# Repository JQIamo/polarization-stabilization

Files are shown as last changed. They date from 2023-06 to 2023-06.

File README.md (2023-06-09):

# polarization-stabilization
## Project Outline
This project explores polarization drift in optical fibers and methods for an active compensation system with wavelength division multiplexing. The applications are to long distance quantum communication with polarization-encoded photonic qubits.

## Folder Contents
- Reports:
  - PHYS407_Final_Report.pdf: Summary of project progress through December of 2022. This includes the first round of single wavelength measurements and two wavelength(PMD) measurements.
  - FIO_LS Presentation.pptx: presentation given October 2022 at FIO/LS meeting in Rochester NY
- Polarimeter: documentation for telecommunication polarimeter
  - Polarimeter_Manual.pdf: Describes method of operation, how to use and how to calibrate
  - Electronics: KiCad project files for the Teensy motherboard and photodiode transimpedance amplifier boards
  - Motherboard Box: contains part list, front panel cutout and pcb spacers
  - Photodiode Casing Cage Mounted: FreeCAD and .stl files for the photodiode detector housings
- Scripts
- Single wavelength measurements: All single wavelength measurements made from summer 2022 through spring 2023 are included with a jupyter notebook that performs an analysis.
- PMD Wavelength Measurement: two wavelength measurements made in fall 2022 and analysis script

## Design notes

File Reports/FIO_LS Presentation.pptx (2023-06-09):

## Polarization Drift Compensation for Long Distance Quantum Communication In Optical Fibers

Deven Bowman, Patrick Banner, Deniz Kurdak, Yaxin Li, Trey Porto, Steven Rolston
University of Maryland College Park

## Introduction

- Long distance quantum communication is key to the future of quantum technologies.
- Polarization-encoded photonic qubits are a possible medium for quantum state transportation
  - Easy to apply rotations
- Major problem: polarization drift in optical fibers
  - Mechanical stresses
  - Temperature fluctuations
  - Manufacturing defects

## Drift Compensation System: Overview

- Our system has 3 major parts: input states, polarization analyzer, and the polarization controller.
- I will describe the design/calibration of the polarization analyzer and results of polarization drift measurements.

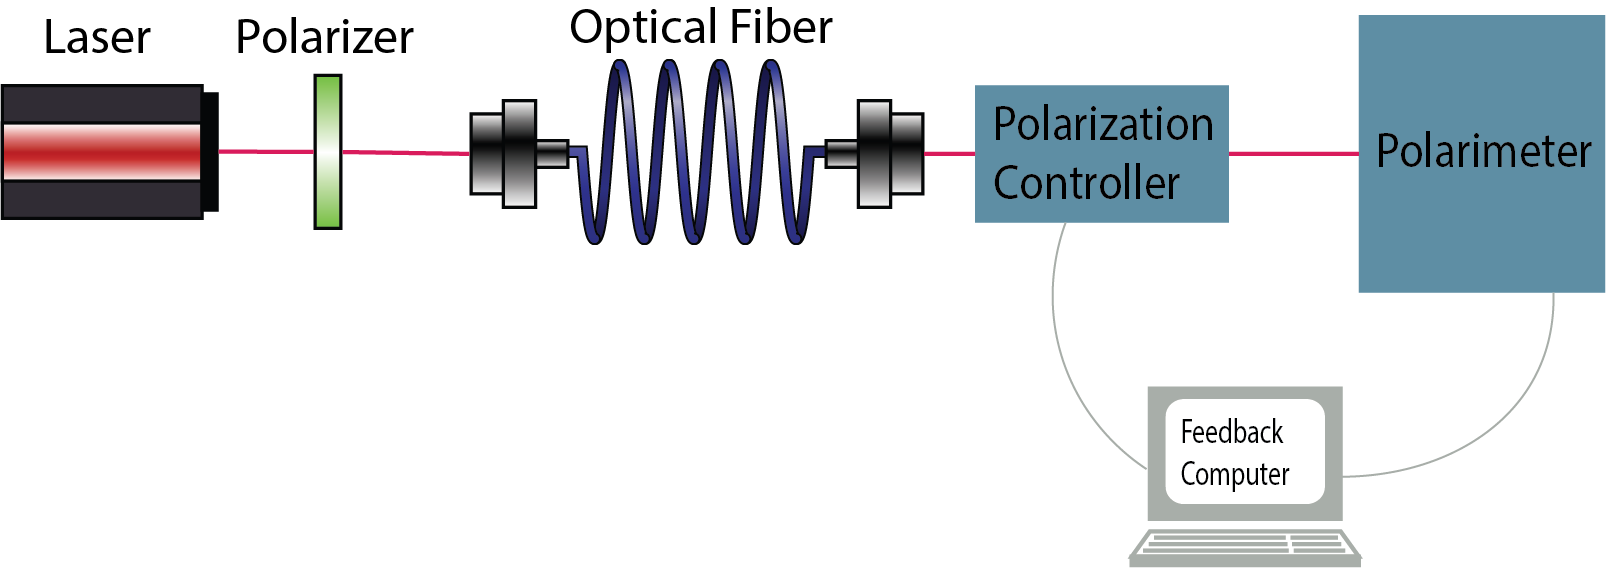
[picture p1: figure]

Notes: Maybe remove text and enlarge image.

## Polarimeter Design

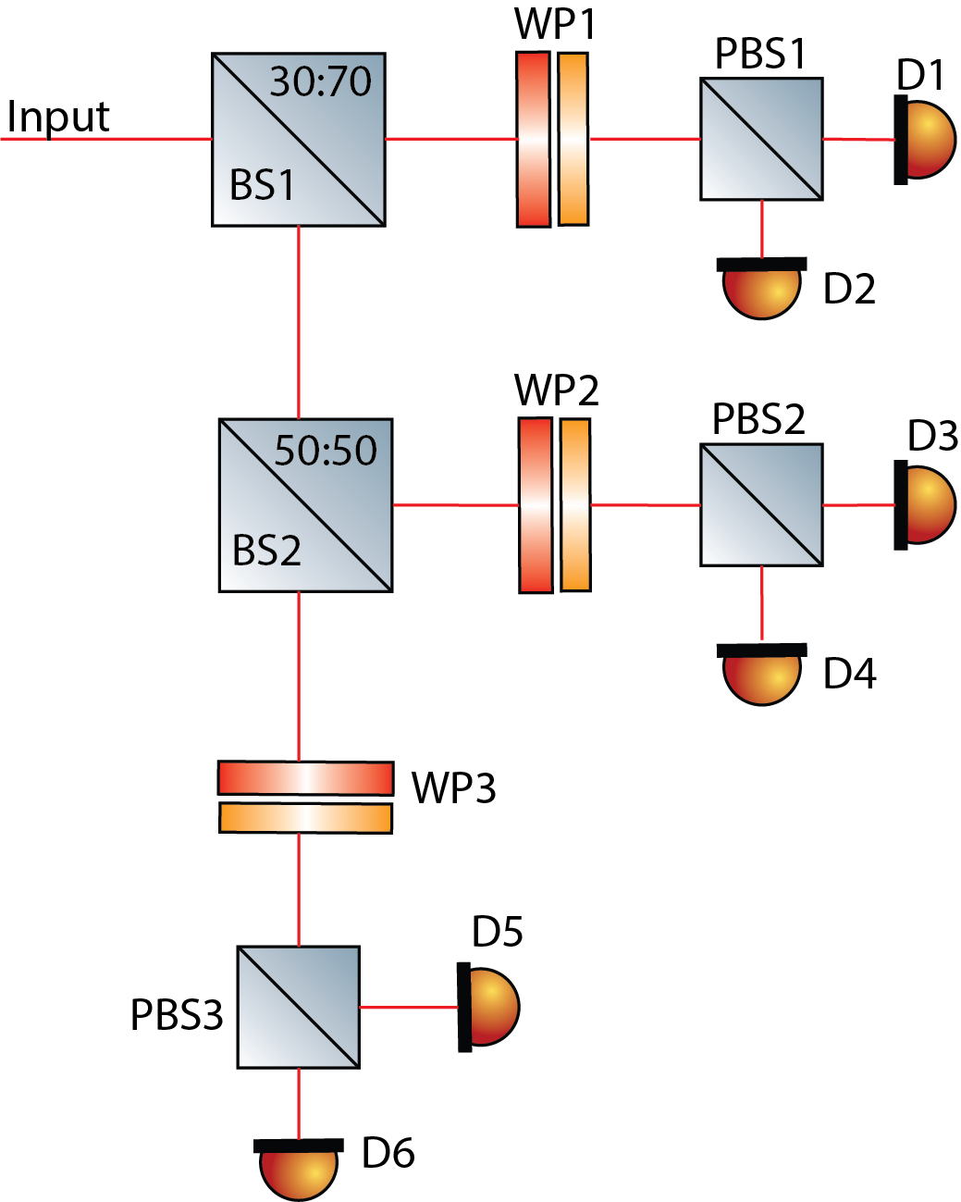
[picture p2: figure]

- 3 detection arms
- polarizing beam splitters project H and V components into separate detectors.
- preceding waveplates “realign” these projection axes

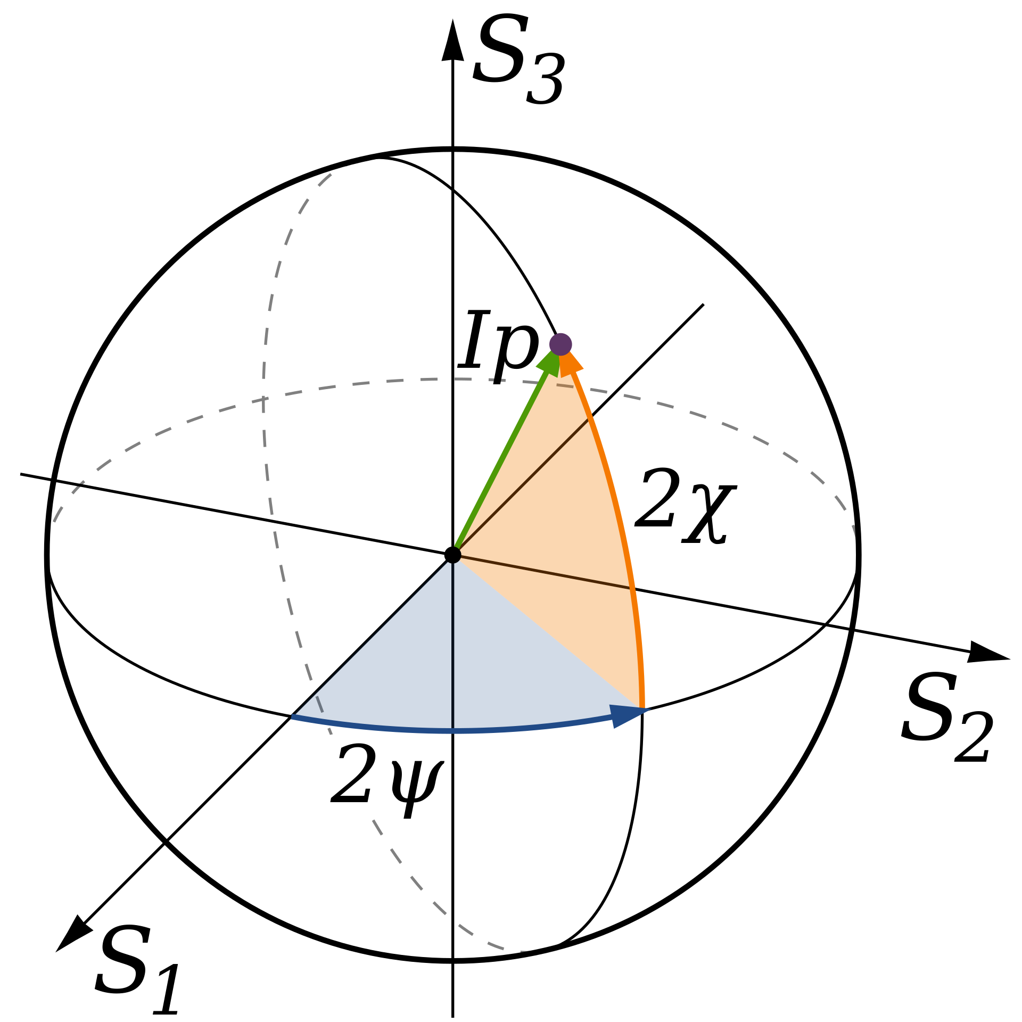
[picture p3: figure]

By Inductiveload - Own work, Public Domain, https://commons.wikimedia.org/w/index.php?curid=4251521

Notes: Adjust diagram: move bottom arm down and add splitting ratio of BS
Perhaps poincare sphere diagram.
Perhaps less words

## Polarimeter Calibration

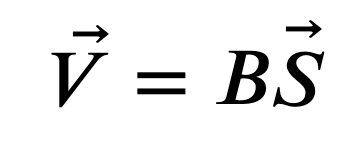
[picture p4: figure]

- Our procedure is based on one presented by Azzam and Lopez, J. Opt. Soc. Am. A(1989).
- The measured state is linearly related to the input state.
- With the Moore-Penrose inverse of this matrix, we can calculate the input states from measurement.

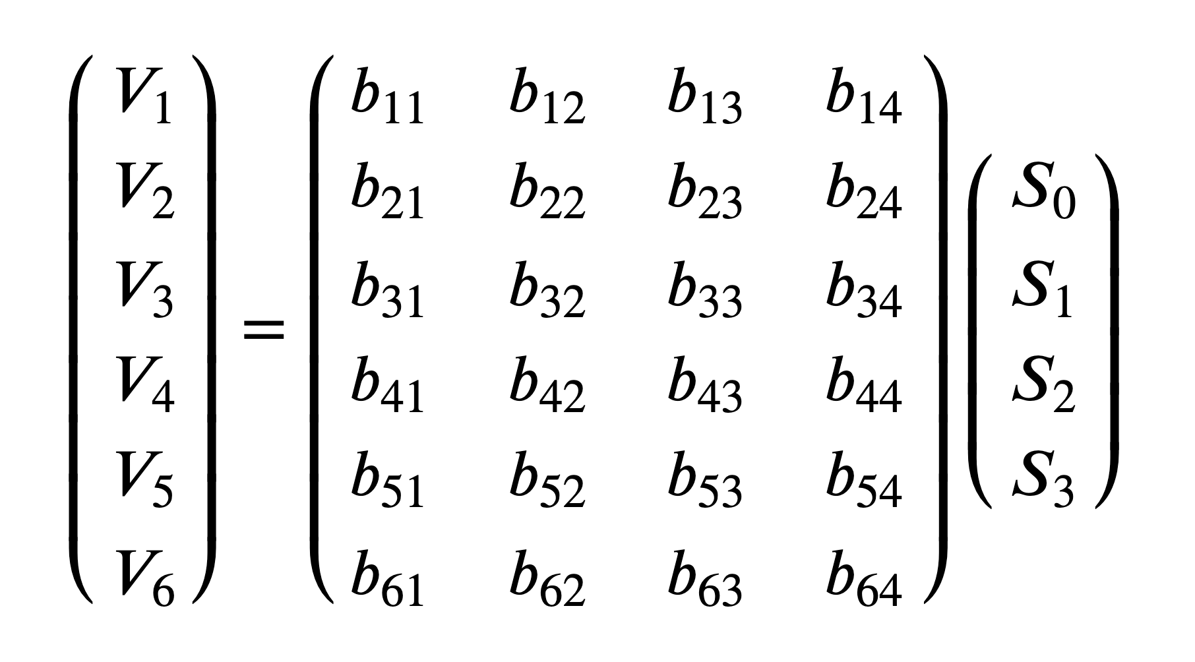
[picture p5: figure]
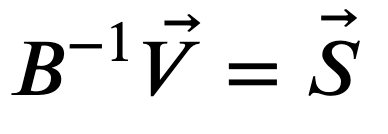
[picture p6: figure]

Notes: Add stokes param slide.

## Calibration Data

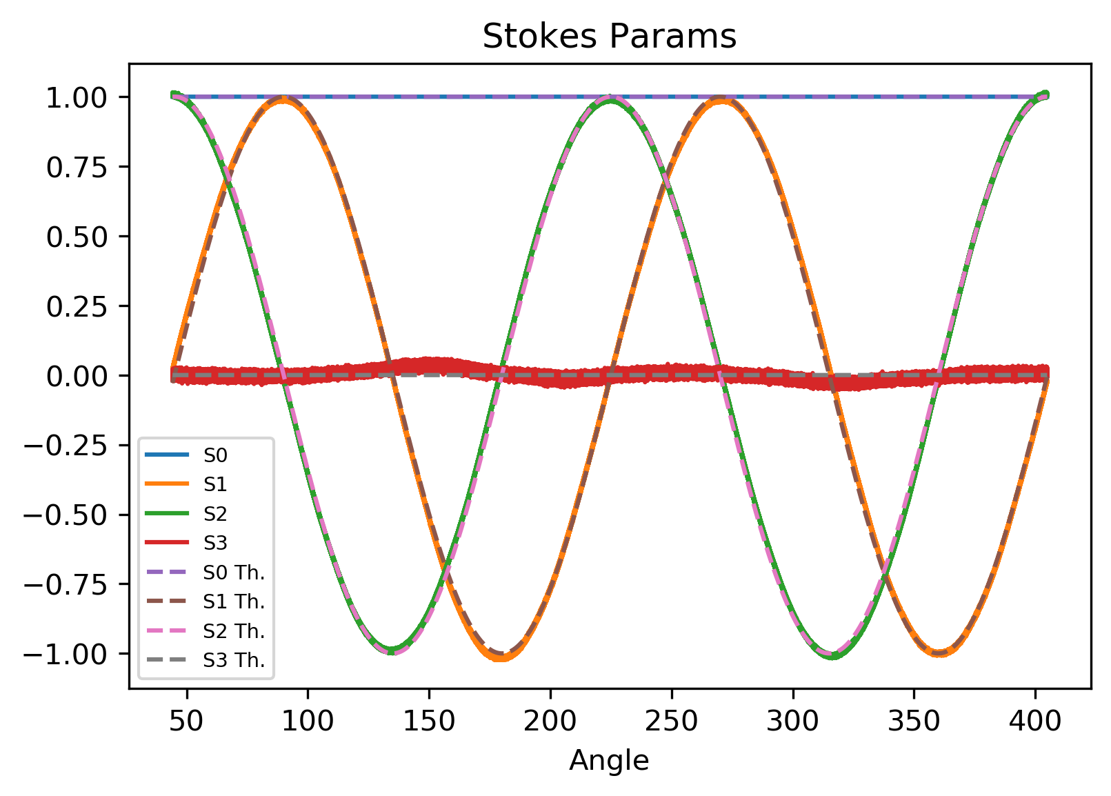
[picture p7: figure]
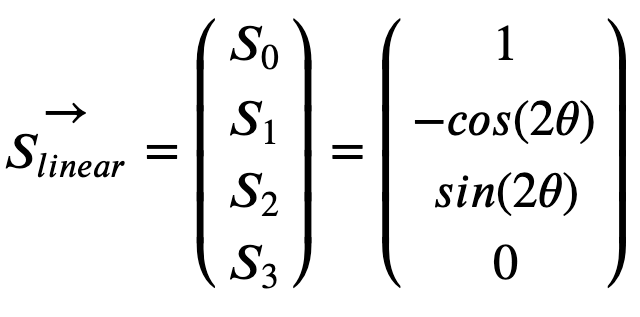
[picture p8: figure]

- A linear polarizer on a motorized rotation mount was used to send in calibration states.
- theoretical Stokes Parameters(dashed lines), calibrated measurements(solid lines).

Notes: Decrease text and move equation

## Polarimeter System

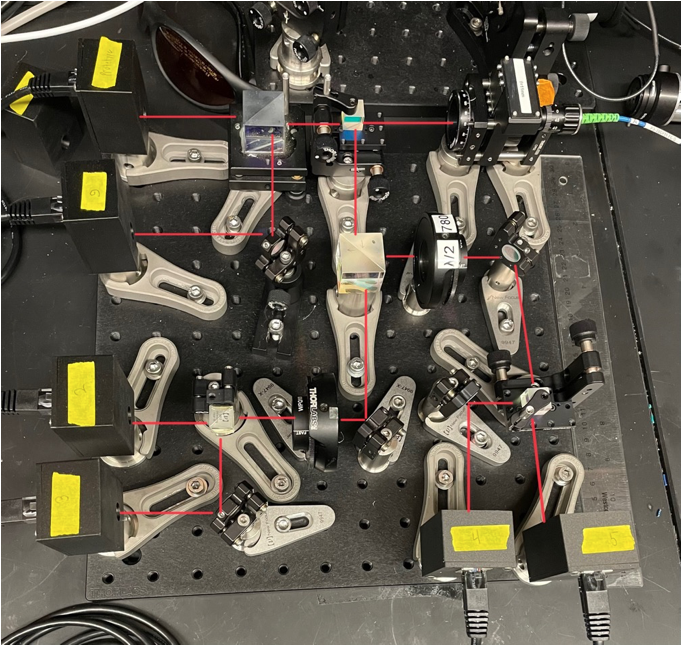
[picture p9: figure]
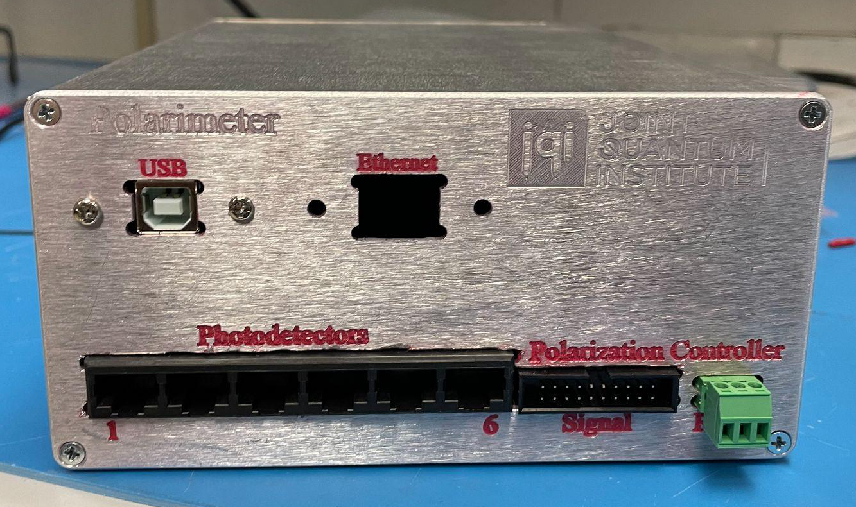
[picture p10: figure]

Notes: Combine with following slide and make more concise. Make read lines bold

## University of Maryland to Army Research Labs fiber link

- UMD and ARL are connected by 2 ~13km fiber optic cables. They are connected on the ARL side for a ~26km fiber loop.
- This fiber provides an optimal test bed for our system.
- Measurements were taken to measure the polarization drift in this fiber. Several other preliminary measurements were conducted for comparison.
- A constant polarization state was launched into the fiber and the polarization was measured on the output by the polarimeter.

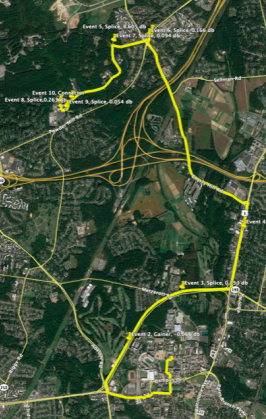
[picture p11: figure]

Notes: Trim words

## Polarization Drift Traces

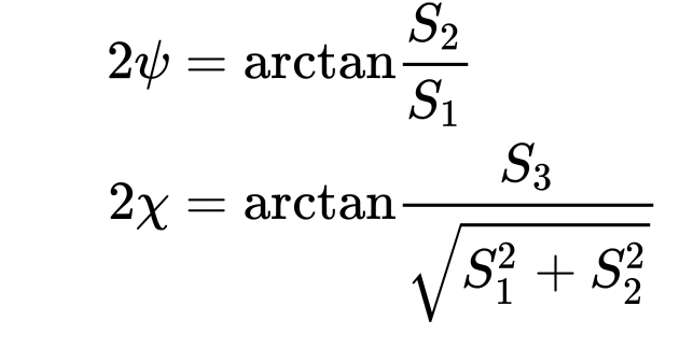
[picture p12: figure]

Direct Connection

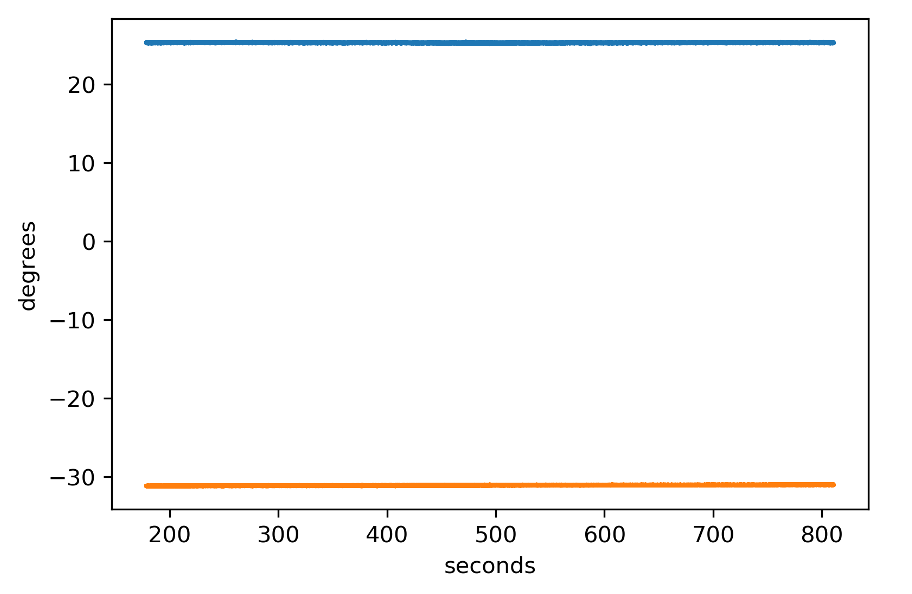
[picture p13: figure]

26km UMD-ARL Fiber

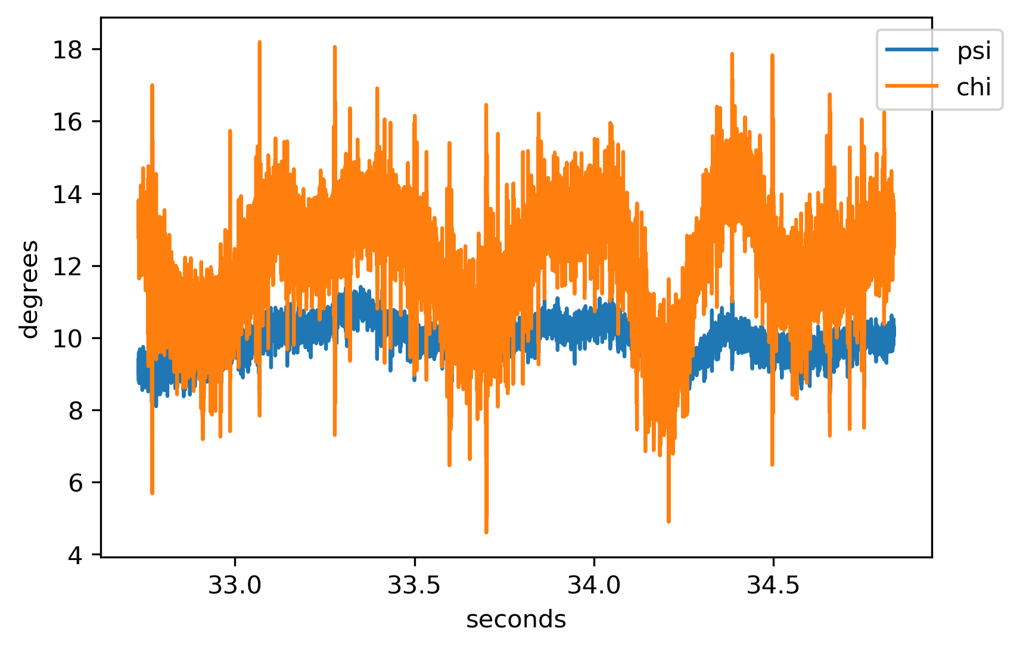
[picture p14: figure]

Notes: Trim words

## Drift Speed Analysis

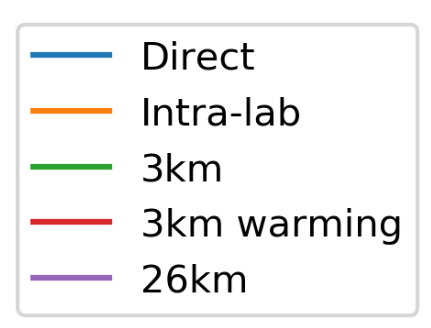
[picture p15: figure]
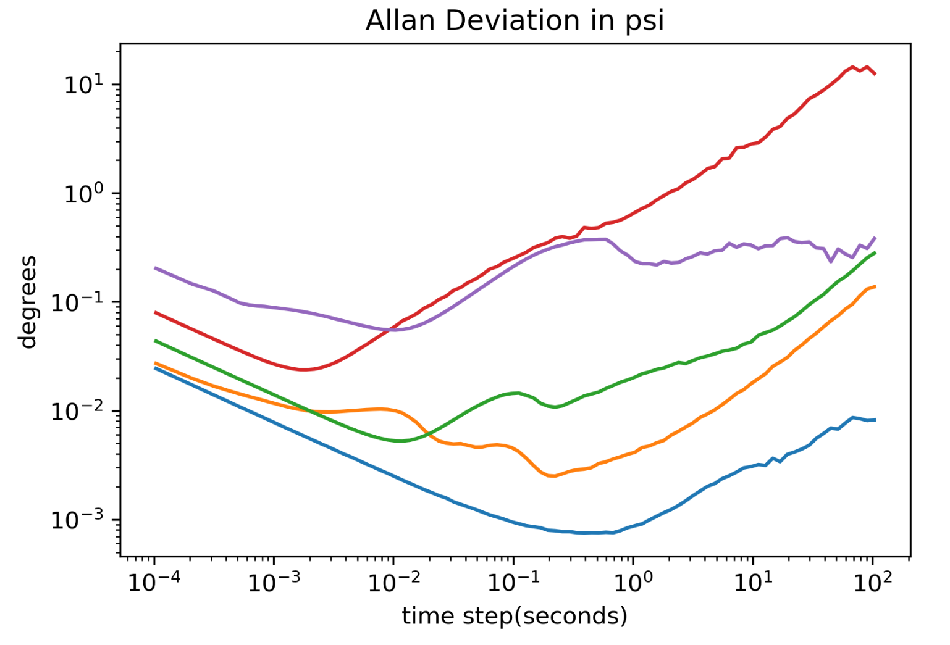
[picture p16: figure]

- An Allan Deviation analysis was conducted.
- Standard deviation between averages over windows of duration τ.

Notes: Don’t try to explain all the lines or to explain allan deviation too technically.

## Going Forward

- Polarization controller feedback algorithm
- Integrate the drift compensation system into a quantum
  - Wavelength Division Multiplexing
  - Polarization Mode Dispersion measurements

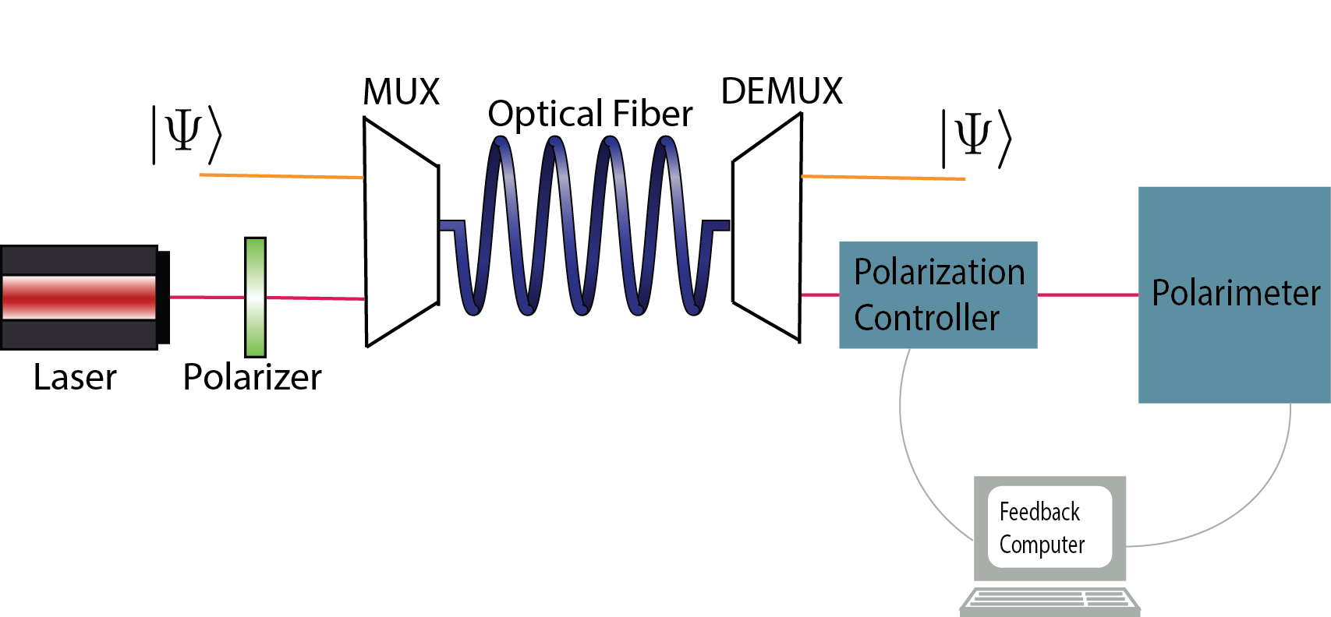
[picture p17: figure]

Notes: Possible a WDM graph?

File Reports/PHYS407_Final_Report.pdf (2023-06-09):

# Polarization Drift Measurements in Optical Fibers for Long Distance Quantum Communication

### Deven Bowman

### June 4, 2023

## 1 Abstract

Polarization drift in optical fibers is studied in the context of developing a polarization drift compensation system for quantum networking atomic systems with > 100 ns long photons. A 26 km fiber, deployed in an urban setting, is used to provide a realistic case study of the polarization drift that will be encountered when trying to achieve long distance entanglement. The rate of polarization drift at one wavelength, 1560 nm, is measured and then compared to measurements of the relative polarization drift between two well separated wavelengths, 1560 nm and 1650 nm.

## 2 Background

Polarization encoded photonic qubits are a natural candidate for a quantum system that can be used to connect nodes of a quantum network. Photons at telecommunication wavelengths can be sent long distances through optical fibers and the transverse modes of polarization form a true two level system that can act as a qubit. Furthermore, qubit operations can be applied with wave plates, an easy to use and ubiquitous technology. This investigation will explore one of the challenges posed to the implementation of polarization qubits, polarization drift in optical fibers.
In general, the polarization state of light is not preserved through optical fibers. Due to mechanical stresses, temperature fluctuations, and manufacturing defects, optical fibers have random birefringences that may vary with time. This leads to the phenomenon of polarization drift and will contribute systematic uncertainty to measurements of the quantum states sent through the fiber. Therefore, understanding and controlling this is of particular interest for efforts to achieve long-distance quantum communication utilizing polarization-encoded photonic qubits.
A polarization drift control system requires several basic elements. Known polarization reference states need to be sent through the fiber under study. The output states are then measured to drive a programmable polarization controller to apply the correct compensating transformation. A major difficulty is to achieve this without interfering with single photons of the quantum channel at their specific wavelength through the same fiber. Previous attempts have addressed this problem by alternating between transmitting single photons and

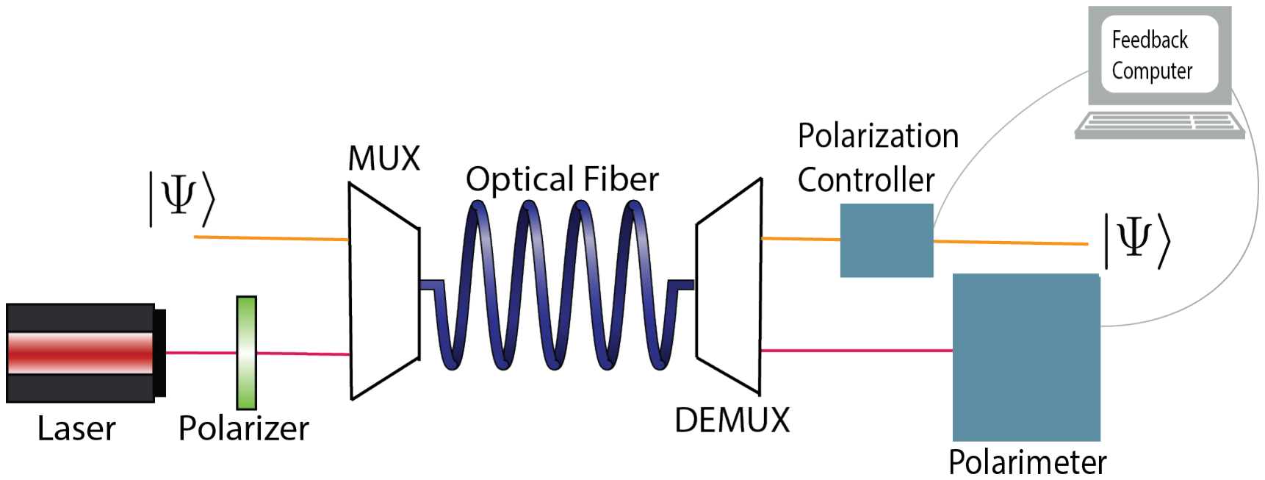
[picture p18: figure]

Figure 1: A wavelength division multiplexing polarization drift control system for quantum communication is displayed. One wavelength is used as the quantum channel while polarization reference states are transmitted at a different wavelength.

transmitting bright reference-state light to stabilize the polarization drift [Wu+06]. If the polarization drift occurs on short time scales, the single-channel method requires interrupting the qubit channel frequently. An alternative method, displayed in Figure 1, is to send reference states at a different wavelength and use wavelength division multiplexing (WDM) so that reference states and qubits are simultaneously transmitted for uninterrupted stabilization.
There are two major concerns for a WDM system: isolation between channels and the wavelength dependence of polarization drift. A milliwatt laser at telecommunication wavelengths, reasonable for transmitting reference-state light, produces ∼ 10¹⁵ photons per second. To multiplex this with a single-photon signal requires wavelength filtering with many orders of magnitude of extinction, which can be improved by increasing the wavelength separation, ∆λ. But, polarization drift varies with wavelength and, with large enough ∆λ, becomes uncorrelated after a time, requiring the transformation matrix relating output states on either channel to be remeasured at repeated intervals [KBA00].
WDM systems have been demonstrated with ∆λ = 0.8 nm, small enough to maintain correlation[Xav+08]. To achieve sufficient isolation with such a small separation, Xavier et al. worked with nanosecond length photons and ignored all signals outside of the expected ns-long windows. Atomic systems typically produce photons 10²
- 10⁴
times longer, requiring
increased wavelength filtering by these factors, achievable with a larger ∆λ. Therefore, an investigation into a polarization drift compensation system using WDM with ∼ 10 − 100 nm separation between channels is well motivated and the development of such a system will address a barrier to the integration of atomic systems, ideal for quantum memories and processors, into quantum networks.
In this analysis, we will adopt 1◦ as the important threshold for a polarization drift compensation system to maintain as the upper bound on polarization drift.
Two sets of measurements were performed in this investigation. I measured the magnitude and rate of polarization drift at one wavelength. Next, I measured the relative polarization drift between two wavelengths. The implications of the results to polarization drift compensation systems for quantum networking are discussed and further steps that can be taken to improve this work are suggested.

## 3 Theory

The Stokes parameter description of polarization uses 4 intensity based metrics to fully describe any full or partially polarized state. Stokes parameters are based solely on observables which makes them the description to use when measuring a polarization state.

S⃗ =

S0
S1
S2
S3

(1)

These 4 parameters in Eq. 1 are calculated with simple intensity measurements. S0 is the total intensity of the light. S1 measures the tendency of light to be horizontally polarized(H), S1 > 0, or vertically polarized(V ), S1 < 0. S2 measures the tendency of the light to be linearly polarized in the 45◦ or −45◦ directions with S2 > 0 or S2 < 0 respectively. S3 describes the tendency of the light to be right circularly polarized(R), S3 > 0, or left circularly polarized(L), S3 < 0. A Stokes vector can be written from these parameters to represent any pure or mixed polarization state.

### 3.1 Pure Polarization States

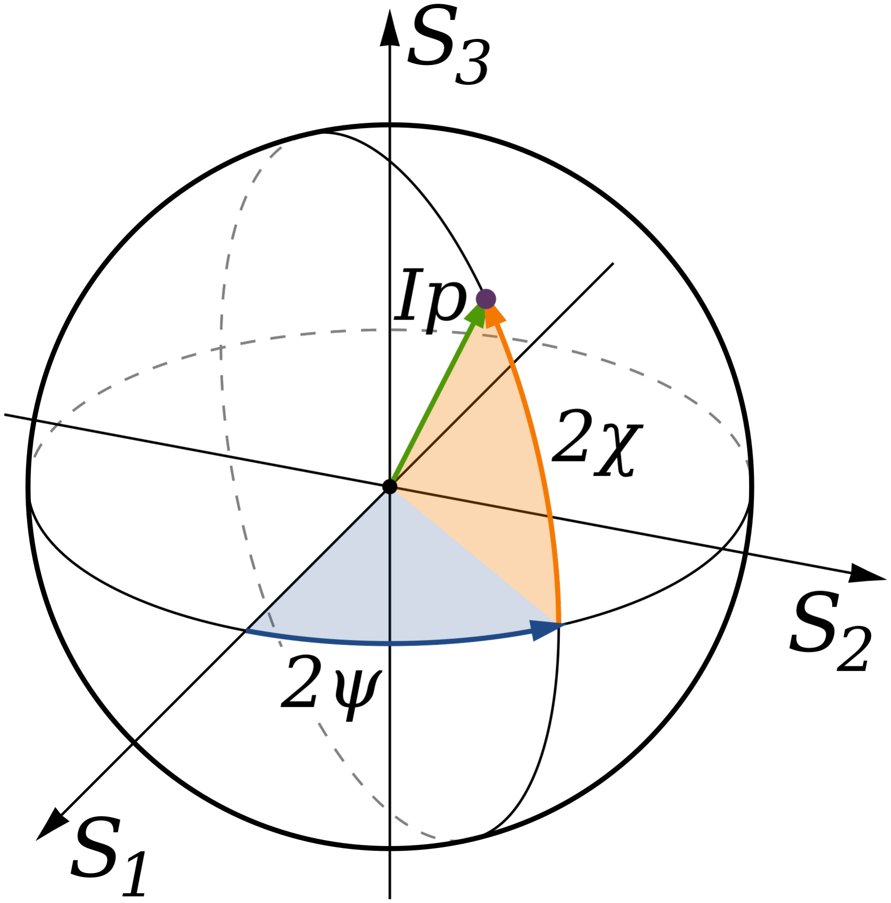
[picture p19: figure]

Figure 2: The Poincare sphere and polarization ellipse angles ψ and χ are displayed.

For pure states, we have the property that S

2
0 = S

2
1 +S

2
2 +S

2/3. As a result, Stokes vectors are often normalized by S0 and reduced to a 3D unit vector.

S⃗ =

1
S0

S1
S2
S3
- (2)

It follows that the set of all pure polarization states can be mapped to a sphere. This mapping is known as the Poincare sphere and is displayed in Figure 2. States on the Poincare sphere can be more concisely represented in terms of two angles.

ψ =

1
2

arctan

S2
S1

, ψ ∈ {0

◦

, 180◦
} | (3)

χ =

1
2

arctan p

S3
S

2
1 + S

2
2

, χ ∈ {−45◦

, 45◦
} | (4)

These angles are formulated to describe the polarization ellipse, but 2ψ and 2χ are the spherical coordinate angles on the Poincare sphere. The factors of two represent that the same polarization state is represented when the polarization ellipse is rotated by 180◦ and when the semi-major and semi-minor axes are swapped.
For the polarization drift and relative drift measurements, we assume that all states are purely polarized since they are generated by laser sources.

## 4 Single Channel Polarization Drift

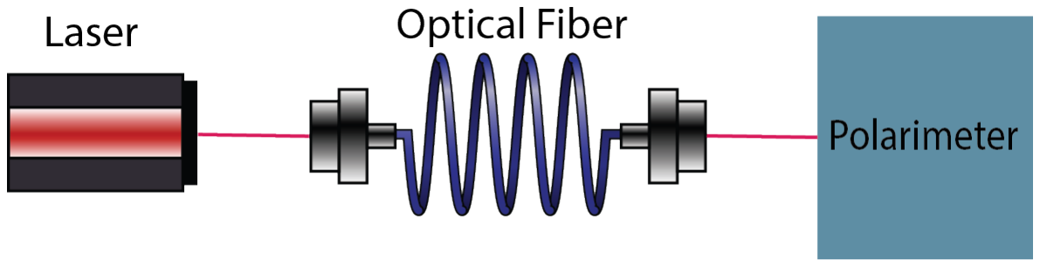
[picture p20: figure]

Figure 3: Schematic for the single channel polarization drift measurement.

To study the rate and magnitude of polarization drift in optical fibers, the experimental setup shown in Figure 3 was used where the length and environmental conditions of the optical fiber was varied. In each measurement, a constant reference state was sent through the fiber with a 1560 nm wavelength laser and the polarization was measured ∼ 10, 000 times per second by a polarimeter custom built for this measurement.

### 4.1 Polarimeter

A six detector Stokes polarimeter was constructed with the schematic depicted in Figure
4. This design uses six intensity measurements that we can relate to the Stokes parameters through a calibration matrix. The photodiode detectors are paired into three detection arms. Light incident on the polarimeter is split into these 3 detection arms by two non polarizing beam splitters, BS1 and BS2. Each detection arm has a series of wave plates, depicted as WP1, WP2 and WP3, that apply transformations to the polarization state before reaching a polarizing beam splitter, PBS1, PBS2, and PBS3, that transmits the projection of the state onto the vertical axis and reflects the projection onto horizontal axis. Finally, a pair of photodiode detectors measures the intensity at each output port of the polarizing beams splitters and produces a voltage signal. While all the PBS’s take projections onto the horizontal and vertical, when combined with the preceding wave plates we can realign their projection axes. The Stokes parameters describe the polarization state relative to 3 linearly independent axes. Therefore, we need to set the wave plates to give us 3 linearly independent projection axes for the different detector arms. Furthermore, the farther we can spread the projection axes in Stokes space, the better the resolution we can achieve. To calculate the

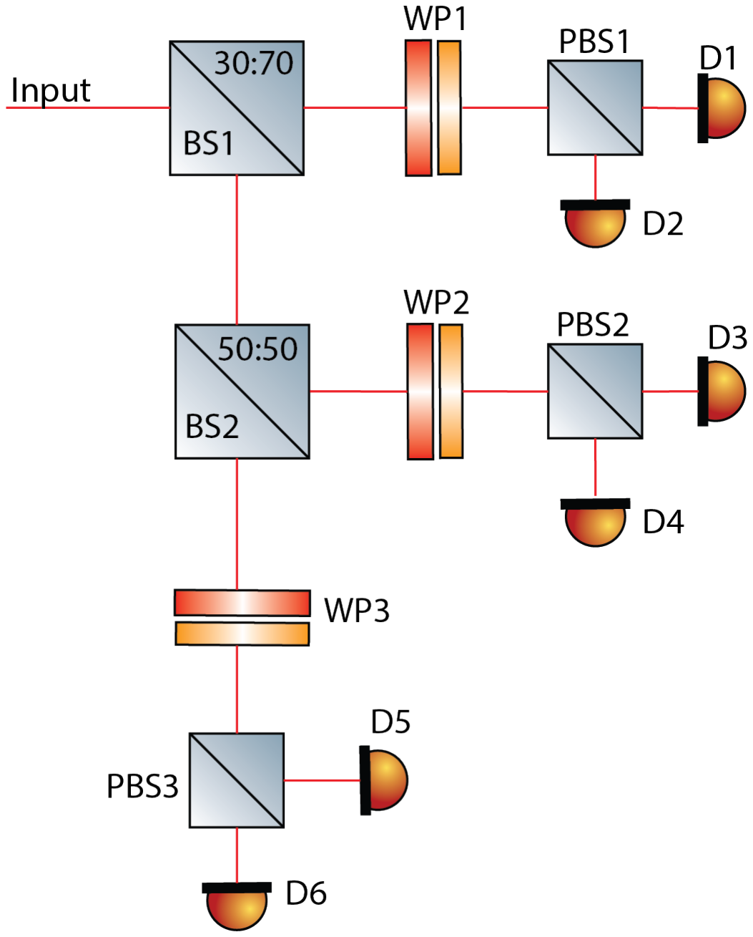
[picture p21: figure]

Figure 4: The design for the Stokes Polarimeter uses several beam splitters (BS), waveplates (WP), polarizing beam splitters (PBS), and photodiode detectors (D) to measure the four Stokes parameters.

Stokes parameters from the output voltage signals we generate a matrix from a calibration procedure similar to that presented by Azzam and Lopez[AL89]. For a polarization state with Stokes vector S⃗, the polarimeter will generate 6 voltages we can write in a vector V⃗ . The two are related by a 6 x 4 matrix B.

V⃗ = BS⃗ | (5)

By generating well defined input polarization states, S⃗ and then measuring the resulting V⃗ , B can be determined. This process was performed in 2 stages. First, a linear polarizer was used to generate a series of known linear polarization states. The input polarization state can be calculated with the angle of the transmission axis of the polarizer from vertical θ with

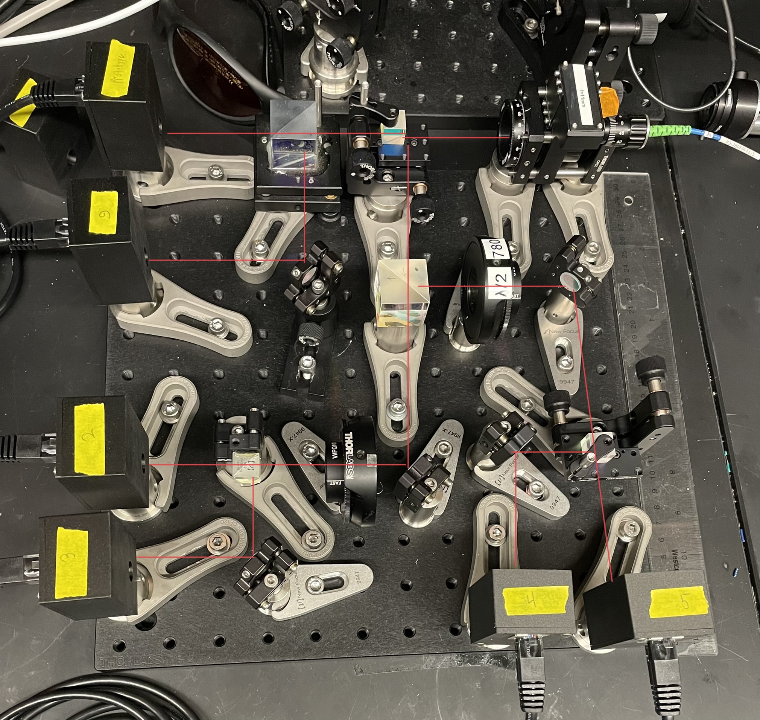
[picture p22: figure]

Figure 5: The 6 detector Stokes Polarimeter is displayed with the optical path drawn as a red line for illustration purposes. The light enters the polarimeter from the fiber launch in the top right. The beam is divided into 6 different paths and the resulting intensities are measured by the photodiode detectors in the black boxes.

Equation 6.

S⃗
linear =

S0
S1
S2
S3

=

1
−cos(2θ)
sin(2θ)
0

(6)

From equations 5 and 6, the i th component of V⃗ can be expressed as a linear combination of matrix elements bij .

vi = bi1 − bi2cos(2θ) + bi3sin(2θ) | (7)

I used a linear polarizer with a measured extinction ratio of > 1000 : 1 and the orientation of the transmission axis known to ∼ ±0.25◦
. The linear polarizer was mounted in a motorized rotation mount and rotated continuously through 360◦ at a rate of 1◦ per second. The polarimeter recorded measurements at 10,000 Hz. A chi squared fit to the measured vi was used to determine the bij matrix elements.
The second stage of the calibration requires input states with some known ellipticity. For this, a procedure, presented in [AL89], was used to account for the error in these input states. First, a linear polarizer and a quarter waveplate were aligned with the transmission axis of the former rotated by 45◦
from fast axis of the latter. In practice, this produces a nearly circular state. Represented on the Poincare sphere, this state is slightly displaced from one of the poles. Then, by rotating both the linear polarizer and the quarter waveplate by 90◦
, the input state is rotated by 180 degrees around the north-south axis of the Poincare sphere. These 2 states are displaced from the pole by a small amount in opposite directions. By averaging the polarimeter measurements associated with each input state, the detector response to a perfect circular state can be attained. By using these calibration measurements, B was calculated which allows the input states to be calculated from the measured voltage states: B

−1V⃗ = S⃗. This calibration matrix, B
−1
, was applied to the voltage states measured from the linear input states. The results are compared to the theoretical values in Figure
6. Good agreement can be seen between the theoretical curves and the measured curves for the normalized Stokes parameters.

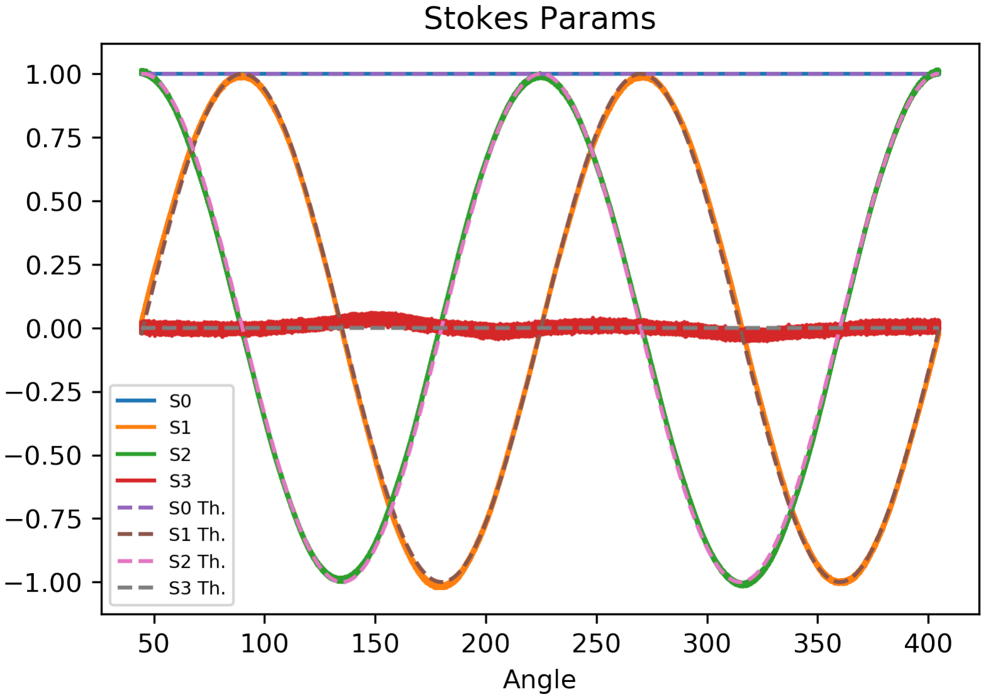
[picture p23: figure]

Figure 6: The normalized Stokes parameters are graphed. The measured parameters are solid lines and the theoretical parameters are dotted lines.

### 4.2 Drift Measurement Procedure

Between the U.S. Army Research Labs(ARL) in Adelphi Maryland and the Atlantic Building at the University of Maryland College Park, there are 2 ∼ 13km fiber connections. Currently these fibers are optically connected at ARL. This 26km fiber, deployed in an urban setting, will be the focus of this stabilization system. A ∼ 2s trace of the polarization data is presented in Figure 8. The polarization state is represented in terms of the angles ψ and χ on the Poincare sphere. A measurement was also taken through a 3 km fiber spool. Measurements were made when the fiber was undisturbed and also when the fiber was forcibly warmed. A trace of the data from the warming trial can be seen in Figure 9. In addition, measurement was made through a fiber connection that stretched across the lab and back to the polarimeter. This was intended to allow for a comparison between the drift in exposed and buried fibers. Only slow drift on the minute time scale was observed in the intra-lab fiber connection. In the final measurement, the polarization drift was measured with the shortest possible connection between the laser source and the polarimeter to provide a baseline for noise inherent to the laser source and the polarimeter. No drift is perceptible in trace from the direct connection configuration, displayed in Figure 7. As a result, our measurements of the polarization drift will have very low systematic uncertainties.

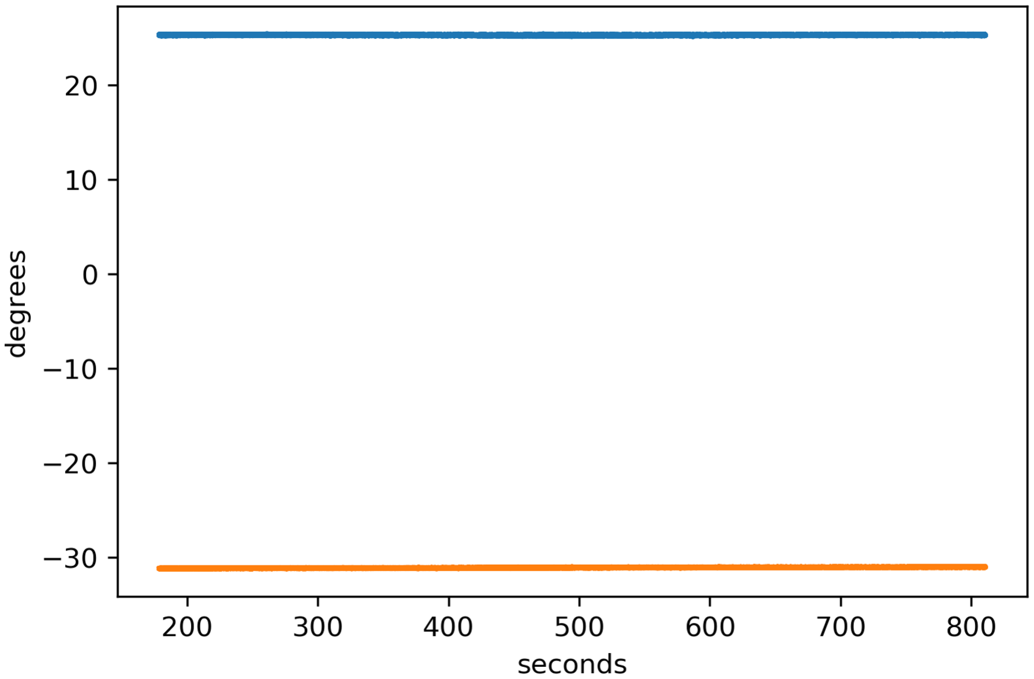
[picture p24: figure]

Figure 7: The output polarization state as a function of time is graphed for a constant input state transmitted through a ∼ 3 m fiber connection.


Figure 8: The output polarization state as a function of time is graphed for a constant input state transmitted through the 26km fiber.


Figure 9: The output polarization state as a function of time is graphed for a constant input state transmitted through a forcibly warmed 3km fiber spool.

### 4.3 Allan Deviation Analysis


Figure 10: The Allan deviation of χ for light at 1650 nm is graphed for the various fiber conditions.

To quantify the drift, the Allan Variance was employed. The Allan variance was devised to measure the stability of atomic clocks over a range of time scales. In a more general context, it is useful to quantify the stability of a measurement in the presence of noise processes. The Allan variance is calculated with equation 8.

σ

2

(τ ) = 1
2

(¯yn+1 − y¯n)

2
=

1
2(N − 1)

N

X⁻¹

i=1

(¯yn+1 − y¯n)

2
(8)


Figure 11: The Allan deviation of ψ for light at 1650 nm is graphed with various fiber conditions.

The data is divided into N consecutive windows of duration τ . The measurements are average within these windows to produce ¯yn, for nth window. The squared difference between ¯yn and y¯n+1 is averaged for all N averaged measurements to calculate σ

2
. With a polarization drift control system measuring and compensating on a time scale τ , we can expect the polarization drift in the fiber to contribute, on average, systematic uncertainties to the qubit channel of order σ. Figure 10 and 11 display σ for each angle over a range of τ from 0.1ms to 100s for the various fiber conditions. The uncertainty in the Allan deviation measurements depends on the type of noise, but it can be well approximated by ± √ σ
N+1 where variances between N+1 ¯y are averaged [RH08].
In all configurations, σ initially decreases. This reflects that the dominant source of noise is random fluctuations from a static distribution. In this range, averaging for longer τ reduces the deviation. Beyond a certain τ , the deviation increases due to noise resembling a random walk process. The measurements of the 26 km fiber show that the deviation reaches a minimum at τmin = 0.01 ± 0.0015 s with σmin = 0.1 degrees for χ. The uncertainty in τ was determined by the spacing between the τmin and the adjacent data points. The Allan deviation was calculated at τ values chosen to be roughly logarithmically spaced at integer multiples of the polarimeter’s sample period. A finer spacing of τ values around τmin can be chosen to reduce the uncertainty, but we are primarily interested in establishing the order of magnitude of the time scale of polarization drift. For this τ , N is large giving uncertainty estimate for σmin of ±8 ∗ 10⁻⁶
for σ, far below the needs of this investigation. Therefore, an optimized polarization drift compensation system should drive a polarization controller with measurements of the drift averaged over ∼ 10 ms windows. This will allow for polarization drift to be maintained below 1◦ on the qubit channel.

## 5 Two Channel Relative Polarization Drift

The same input polarization state at two different wavelengths will, in general, transform through the optical fiber to distinct output states for each wavelength. The relationship between these two output states is expected to vary with time, resulting in relative polarization drift. To measure the relative polarization drift between wavelengths, we need to determine the transformation matrix that relates the output states at either wavelength. Two polarization states were sent through the fiber at each wavelength and the output states were measured. The output states were used to calculate the transformation matrix. Sequential measurements of this matrix allow us to determine the time scales over which polarization drift at either wavelength is correlated.
The polarization transformation induced by the optical fiber can be described as a matrix equation.
T

λjS⃗

λj
i = T⃗

λj
i

(9)

T is the 3x3 transformation matrix of the fiber, S⃗ is an input polarization state to the fiber, T⃗ is an output state, and i ∈ {1, 2, 3}, j ∈ {1, 2} with i indexing the polarization states

and j indexing the wavelengths. By choosing linearly independent input states, {s

λj
i

} and
{t

λj
i

} form bases for the output and input spaces. We can choose the input basis states to be S⃗

λj
1

, S⃗

λj
2

, and S⃗

λj
1 × S⃗

λj
2 where states 1 and 2 are orthonormal and × denotes the vector cross product. Since polarization transformations correspond to rotations on the Poincare Sphere, Tλj (S⃗

λj
1 × S⃗

λj
2

) = T⃗

λj
1 | × T⃗ λi
2 | because Tλj | preserves lengths and angles
between vectors. Therefore, only T⃗

λj
1

and T⃗

λj
2 need to be measured at either wavelength to uniquely determine three output states at either wavelength. Then, the transformation matrix between wavelengths can then be calculated.

T⃗ λ2

i | = MT⃗ λ1
| i

(10)

Equation 10 implies the following relation.

B = MA | (11)

Where the A and B matricies are defined as follows.

A =

S⃗λ1
1

, S⃗λ1
2

, S⃗λ1
3
, B =
| - T⃗ λ2
| 1 , T⃗ λ2
| 2

, T⃗ λ2
| | 3
(12)

Then M can be calculated with A⁻¹ .

M = BA⁻¹
(13)

The schematic for the experimental setup is displayed in Figure 12. Lasers at 1560 nm and 1650 nm are each split into two beams by fiber couplers. At each wavelength, polarization controller fiber paddles transform the polarization state of one beam to be linearly independent with the other beam. A Bristol fiber optic switch launches each beam through the fiber sequentially and a PAX1000IR2 polarimeter measures the output polarization states. The PAX1000IR2 measures polarization states in terms of two angles χ and ψ, defined earlier in terms of their relation to the Stokes parameters, with ±0.25 degree uncertainty up to


Figure 12: The experimental schematic to measure relative polarization drift at 1560 nm and 1650 nm is displayed.

a sample rate of 400 Hz. The PAX1000IR2 was used, instead of the Stokes polarimeter, since it was easier to work with at multiple wavelengths and the speed of the switch was much slower, no longer necessitating the need for ultra-fast polarization measurements. The optical switch is rated to switch in < 5 ms with a switching frequency of 30 Hz. In practice, switching between channels every 150 ms was the fastest achievable rate due to unpredictable latency in either the switching or polarization measurement acquisition. With four channels to switch to, M was measured at every 0.6 s. The experiment was controlled by a Python script that communicated with the optical switch and the polarimeter through serial. Data was collected for 30 minutes.
From the measurements of χ and ψ, it was natural to express the states as normalized Stokes Vectors on the Poincare sphere. In this representation, the M is a 3x3 rotation matrix. Therefore, it can be fully described by an axis of rotation ⃗n and a rotation angle θ. Both of these can be determined from the eigenvalues and eigenvectors of the matrix. The eigenvalues are 1, eiθ, and e

−iθ. The eigenvector with eigenvalue 1, V⃗ real, is parallel to the rotation axis and cos(θ) is the real part of either complex eigenvalue, allowing for determination of θ. V⃗
real
was normalized to be equal to ⃗n up to a sign. The polarization states and θ, were observed to vary smoothly. Therefore, the sign of ⃗n was chosen to maintain continuity. Since ⃗n is also a point on the Poincare sphere, it can be concisely represented in terms of two angles, ψ and χ, giving us a total of three angles that encode the M.
An Allan deviation analysis was performed on these three angles to allow for a comparison to the single channel polarization drift. The Allan deviation is expected to present similar trends to that of the single channel drift. For sufficiently small τ , the M will be measured much faster than the rate at which it drifts. In this range, the deviation will decrease as measurements are averaged over longer τ . At some characteristic time scale τmin, the random walk drift will begin to increase the deviation for longer averaging windows. Therefore, τmin for single channel and two channel relative drift allow for a comparison of the time scales of drift. The Allan deviation results are displayed in Figure 13 for 0.6s < τ < 600s. The


Figure 13: The Allan deviation of the two angles that define the rotation axis, χ and ψ, and the rotation angle. These quantities describe relative drift between channels at 1560 nm and 1650 nm.

lower bound is set by the sample rate of the measurement and the upper bound was limited by the duration of the data taking. The Allan deviation of all three angles present local minima at τmin =∼ 2 s but this approaches the sample rate of the measurement. Therefore, the data provides a coarse set of τ from which we can calculate σ. However, it is clear that the increasing slope characteristic of random-walk noise begins on the several second time scale. For these time scales, the average deviation between rotation angles is ∼ 0.4 degrees and, for ψ and χ, is 0.2 degrees. At τ = 2 s, the sum of all angles is less than 1◦
, suggesting
there is a parameter regime that the WDM system in Figure 1 could operate and maintain less than 1◦ polarization drift on the qubit channel.

## 6 Results

It is clear that the polarization drift at 1560 nm and 1650 nm are not correlated for long times. The transformation matrix between the output states at either wavelengths varies in time. However, this variation may be slow enough to allow for a dual channel WDM system to be implemented. Polarization was found to drift on the 0.1

◦
scale over the 10 ms time scale. By comparison, the relative drift between two channels, in terms of the drift of the three angles that define the transformation matrix, was found to drift by tenths of a degree over seconds. A drift control system could take advantage of the correlation between wavelengths for short times to reduce the rate at which the qubit channel needs to be interrupted. In this system, the transformation matrix between the control reference state channel and the qubit channel could be measured every several seconds. In between these measurements, the polarization drift can be continuously measured on the reference state channel to allow for polarization compensation of the qubit channel. During this window, there will be relative drift between the two channels which will increase the systematic uncertainties on the qubit channel. This investigation shows that these additional uncertainties can be expected to be < 1
- on average.

## 7 Continuing Work

The two channel relative polarization drift measurement will provide more definitive results with a faster sample rate for the measurement. This experiment was limited by unpredictable latency in either the response of the optical switch or the PAX1000IR2 to commands.
I am working on a measurement that should identify either the switch or the polarimeter as the issue. A laser will be sent into one of the ports of the switch while the rest will be dark. A function generator will create TTL pulses to drive the switch between the light and dark channels. A photodiode will measure the output signal on an oscilloscope that is also synchronized with the TTL signal. Varying latency in the switching time will generate a signal on the oscilloscope that is unstable when the trigger is set to the TTL signal.
The sample rate will increase by a factor of four by optimizing the current hardware. This will allow us to probe smaller τ for the relative drift and increase the resolution near

τmin.

## References

[AL89] | R. M. A. Azzam and Ali G. Lopez. “Accurate calibration of the four-detector photopolarimeter with imperfect polarizing optical elements”. In: J. Opt. Soc. Am. A 6.10 (Oct. 1989), pp. 1513–1521. doi: 10.1364/JOSAA.6.001513. (https://doi.org/10.1364/JOSAA.6.001513) url: http://opg.optica.org/josaa/abstract.cfm?URI=josaa-6-10-1513.
[KBA00] | Magnus Karlsson, Jonas Brentel, and Peter A. Andrekson. “Long-term measure- ment of PMD and polarization drift in installed fibers”. In: Journal of Lightwave Technology 18.7 (2000), pp. 941–951. doi: 10.1109/50.850739. (https://doi.org/10.1109/50.850739)
[Wu+06] | Guang Wu et al. “Stable polarization-encoded quantum key distribution in fiber”. In: (2006). doi: 10.48550/ARXIV.QUANT-PH/0606108. (https://doi.org/10.48550/ARXIV.QUANT-PH/0606108) url: https://arxiv. org/abs/quant-ph/0606108. (https://arxiv.org/abs/quant-ph/0606108)
[RH08] | William Riley and David Howe. Handbook of Frequency Stability Analysis. en. July 2008. url: https://tsapps.nist.gov/publication/get_pdf.cfm?pub_ id=50505. (https://tsapps.nist.gov/publication/get_pdf.cfm?pub_id=50505)

[Xav+08] G. B. Xavier et al. “Full polarization control for fiber optical quantum communi-
| cation systems using polarization encoding”. In: Opt. Express 16.3 (Feb. 2008), pp. 1867–1873. doi: 10.1364/OE.16.001867. (https://doi.org/10.1364/OE.16.001867) url: https://opg.optica.org/ oe/abstract.cfm?URI=oe-16-3-1867. (https://opg.optica.org/oe/abstract.cfm?URI=oe-16-3-1867)

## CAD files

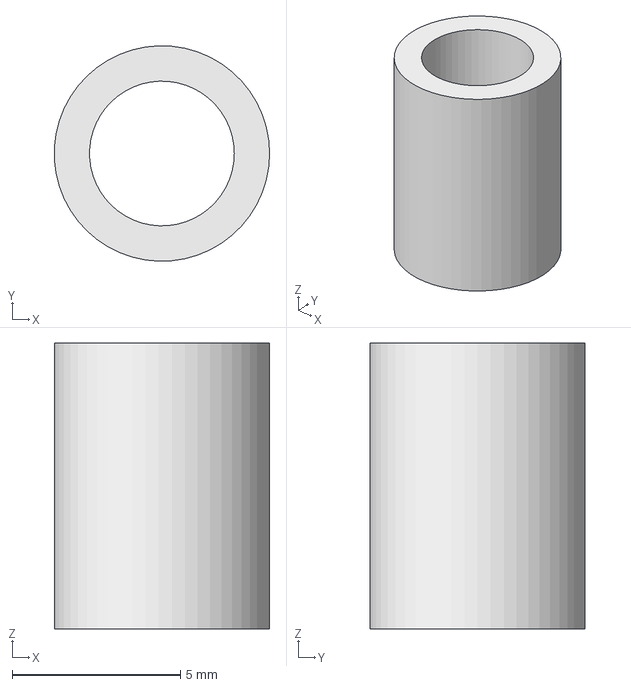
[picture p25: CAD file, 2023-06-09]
Polarimeter/Motherboard Box/PCB Spacers.FCStd
6.39 x 6.40 x 8.50 mm

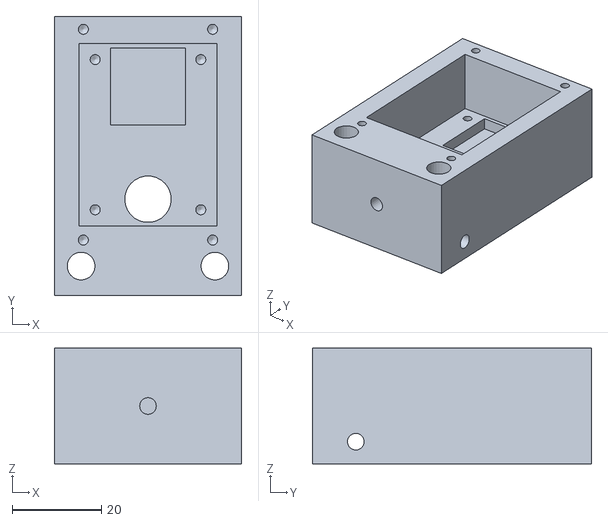
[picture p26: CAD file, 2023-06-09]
Polarimeter/Photodiode Casing Cage Mounted/DiodeCasingCageMounted-Body.stl
42.0 x 62.6 x 26.0

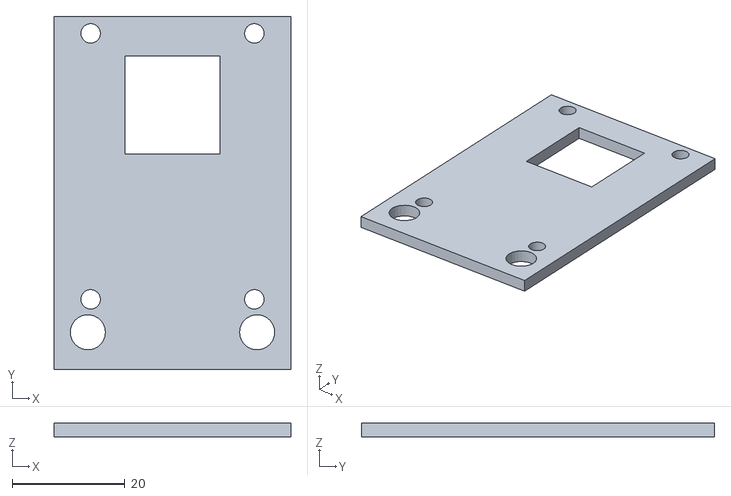
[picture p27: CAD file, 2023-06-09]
Polarimeter/Photodiode Casing Cage Mounted/DiodeCasingCageMounted-Lid.stl
42.0 x 62.6 x 2.50

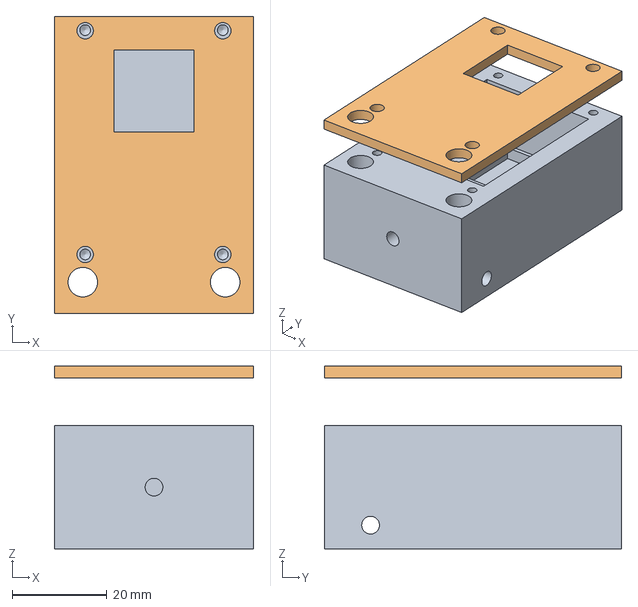
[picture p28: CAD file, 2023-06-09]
Polarimeter/Photodiode Casing Cage Mounted/DiodeCasingCageMounted.FCStd
42.0 x 62.6 x 38.5 mm

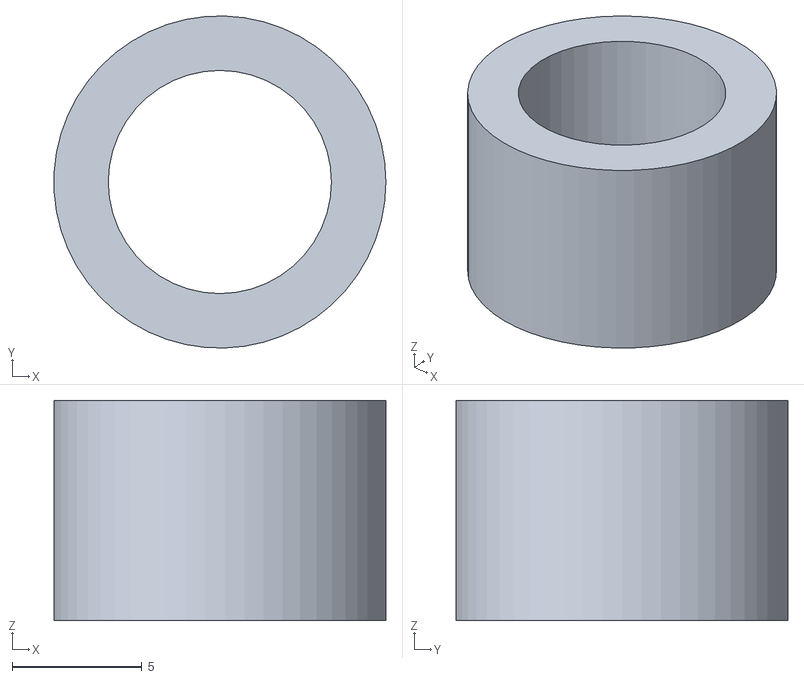
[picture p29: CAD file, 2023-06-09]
Polarimeter/Motherboard Box/PCB Spacers-Body.stl
12.8 x 12.8 x 8.50

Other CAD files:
Polarimeter/Motherboard Box/PCB Spacers-Bodyv2.stl
Polarimeter/Motherboard Box/PCB Spacers-BodySketchv2.stl

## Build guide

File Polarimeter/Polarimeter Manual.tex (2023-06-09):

\documentclass{article}
\usepackage{graphicx} % Required for inserting images
\usepackage{amsmath}  % improve math presentation
\usepackage{gensymb} % added so I have the degree symbol
\usepackage[margin=1in,letterpaper]{geometry} % decreases margins
\usepackage[final]{hyperref} % adds hyper links inside the generated pdf file
\usepackage{physics} %use for mathematical symbols
\usepackage[backend=biber,style=alphabetic,sorting=ynt]{biblatex}
\addbibresource{refs_figures/refs.bib}
\title{Polarimeter Manual}
\author{Deven Bowman}
\date{May 2023}

\begin{document}

\maketitle

\begin{figure}[h]
    \centering
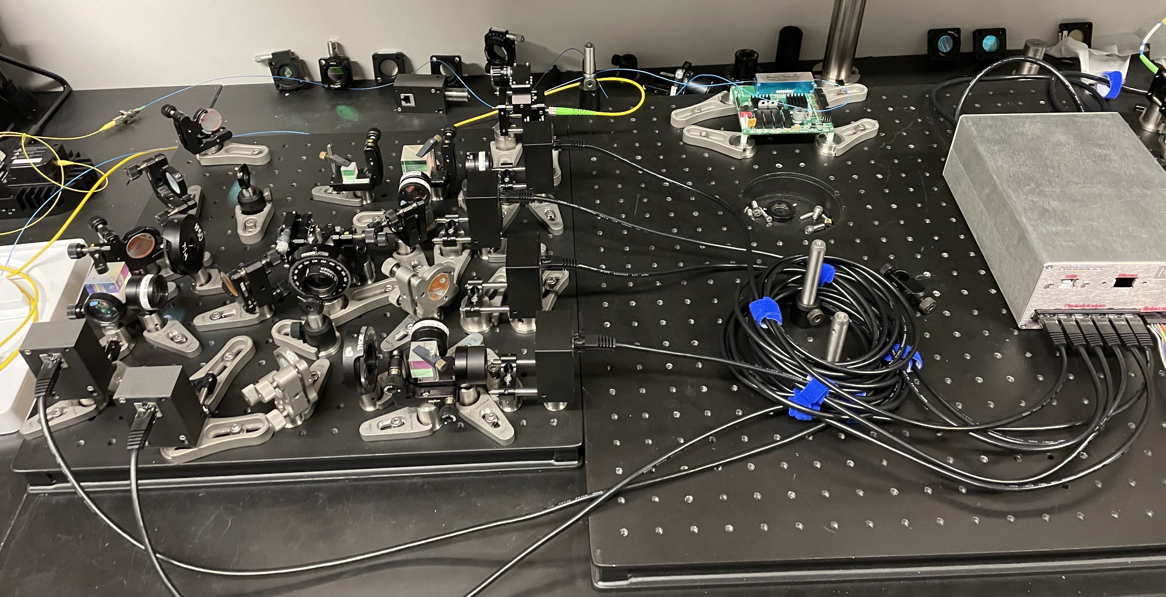
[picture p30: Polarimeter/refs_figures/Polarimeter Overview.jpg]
    
    % \caption{1550 nm polarimeter}
    \label{Polarimeter_pic}
\end{figure}

\section{How it works}
\subsection{A review of Stokes Parameters}
The Stokes parameter description of polarization uses 4 intensity based metrics to fully describe any full or partially polarized state. Stokes parameters are based solely on observables which makes them the description to use when measuring a polarization state.

\begin{equation}
    \Vec{S}= \begin{bmatrix}
    S_0\\
    S_1\\
    S_2\\
    S_3\\
    \end{bmatrix}
    \label{Stokes Vector}
\end{equation}

These 4 parameters in Eq. \ref{Stokes Vector} are calculated with simple intensity measurements. $S_0$ is the total intensity of the light. $S_1$ measures the tendency of light to be horizontally polarized($H$), $S_1 > 0$, or vertically polarized($V$), $S_1 < 0$. $S_2$ measures the tendency of the light to be linearly polarized in the $45\degree$ or $-45\degree$ directions with $S_2 >0$ or $S_2<0$ respectively. $S_3$ describes the tendency of the light to be right circularly polarized($R$), $S_3 >0$, or left circularly polarized($L$), $S_3<0$. A Stokes vector can be written from these parameters to represent any pure or mixed polarization state. 
\subsection{Pure Polarization States}
\begin{figure}[!h]
\begin{center}
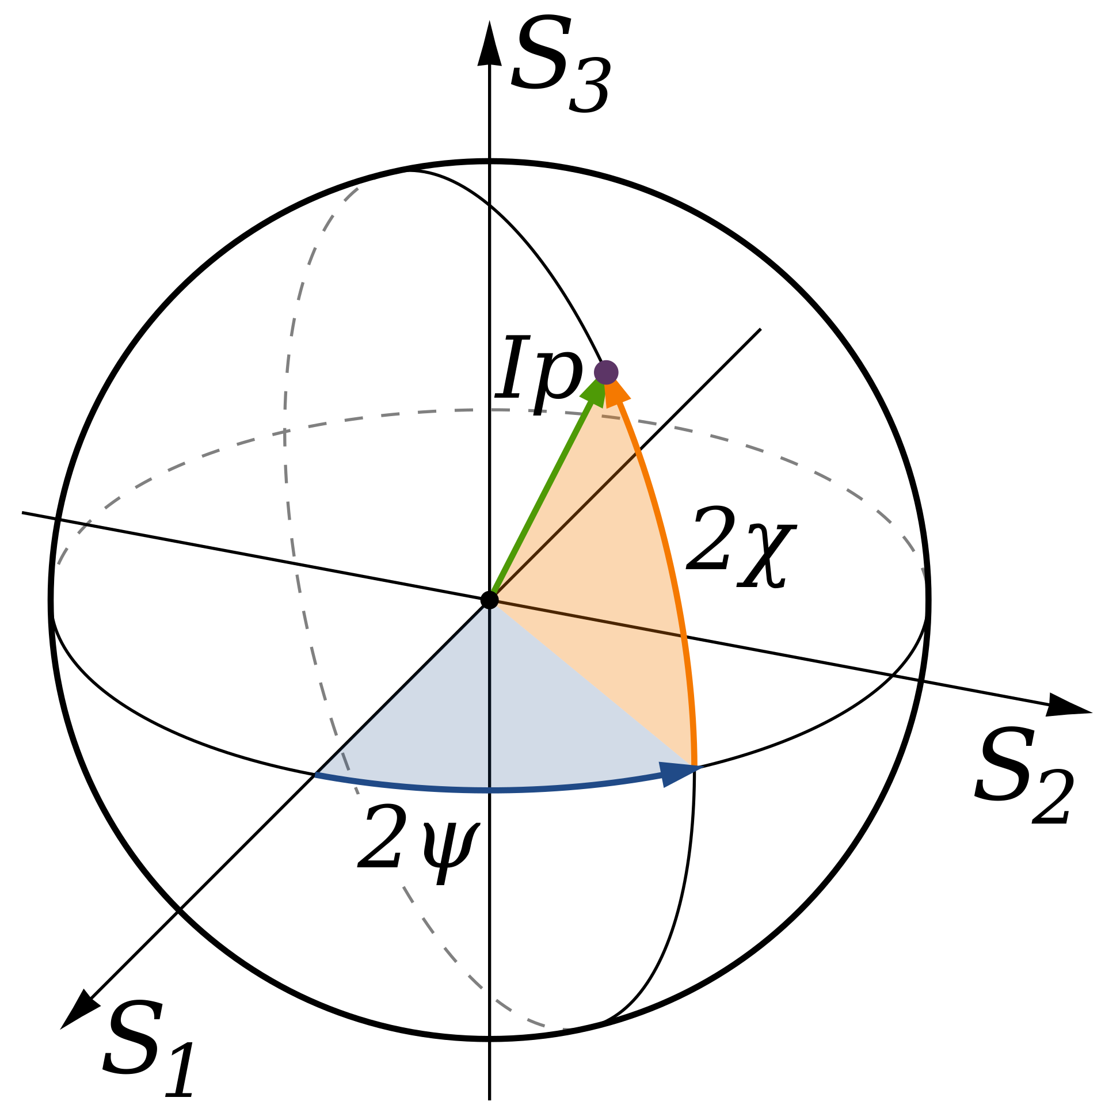
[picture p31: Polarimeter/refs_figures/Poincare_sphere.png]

\end{center}
\caption{The Poincare sphere and polarization ellipse angles $\psi$ and $\chi$ are displayed.}
\label{Poincare Sphere}
\end{figure}

For pure states, we have the property that $S_0^2=S_1^2+S_2^2+S_3^2$. As a result, Stokes vectors are often normalized by $S_0$ and reduced to a 3D unit vector.
\begin{equation}
    \Vec{S}= \frac{1}{S_0}\begin{bmatrix}
    S_1\\
    S_2\\
    S_3\\
    \end{bmatrix}
\end{equation}
It follows that the set of all pure polarization states can be mapped to a sphere. This mapping is known as the Poincare sphere and is displayed in Figure \ref{Poincare Sphere}. States on the Poincare sphere can be more concisely represented in terms of two angles.
\begin{equation}
    \psi = \frac{1}{2}\arctan{\frac{S_2}{S_1}}, \psi\in\{0^{\circ}, 180^{\circ}\}
\end{equation}
\begin{equation}
    \chi = \frac{1}{2}\arctan{\frac{S_3}{\sqrt{S_1^2 + S_2^2}}}, \chi\in\{-45^{\circ}, 45^{\circ}\}
\end{equation}
These angles are formulated to describe the polarization ellipse, but $2\psi$ and $2\chi$ are the spherical coordinate angles on the Poincare sphere. The factors of two represent that the same polarization state is represented when the polarization ellipse is rotated by $180^{\circ}$ and when the semi-major and semi-minor axes are swapped.

\subsection{Polarimeter Design}
The schematic diagram for the polarimeter is shown in figure \ref{Polarimeter Schematic}. This design uses six intensity measurements that are related to the Stokes parameters through a calibration matrix. The photodiode detectors are paired into three detection arms. Light incident on the polarimeter is split into these 3 detection arms by two non polarizing beam splitters, BS$_1$ and BS$_2$. Each detection arm has a series of waveplates, depicted as WP$_1$, WP$_2$ and WP$_3$, that apply transformations to the polarization state before reaching a polarizing beam splitter, PBS$_1$, PBS$_2$, and PBS$_3$, that transmits the projection of the state onto the vertical axis and reflects the projection onto horizontal axis. Finally, a pair of photodiode detectors measures the intensity at each output port of the polarizing beams splitters and produces a voltage signal. The polarization states which the beams splitters project onto is determined by the configuration of the preceding waveplates. The Stokes parameters describe the polarization state relative to 3 linearly independent axes. Therefore, waveplates are set to give us 3 linearly independent projection axes for the different detector arms. Furthermore, the farther spread out the projection axes are in Stokes space, the better the resolution the detector has achieve. 
\begin{figure}[!h]
\begin{center}

\end{center}
\caption{The design for the Stokes Polarimeter uses several beam splitters (BS), waveplates (WP), polarizing beam splitters (PBS), and photodiode detectors (D) to measure the four Stokes parameters.}
\label{Polarimeter Schematic}
\end{figure}

To calculate the Stokes parameters from the output voltage signals, a matrix is calculated from a calibration procedure similar to that presented by Azzam and Lopez\cite{Azzam89}. 

\subsection{Calibration Matrix}
For a polarization state with Stokes vector $\vec{S}$, the polarimeter will generate 6 voltages we can write in a vector $\vec{V}$. The two are related by a 6 x 4 instrument matrix $\textbf{B}$ .
\begin{equation}
    \vec{V} = \textbf{B}\vec{S}
    \label{Calibration eq}
\end{equation} 
By generating well defined input polarization states, $\vec{S}$ and then measuring the resulting $\vec{V}$, the instrument matrix $\textbf{B}$ can be determined. Then, the Moore-Penrose left inverse of the instrument matrix, $\textbf{B}^{+}$ can be calculated.
\begin{equation}
    \textbf{B}^{+} = \textbf{B}^{T}(\textbf{B}\textbf{B}^{T})^{-1}
    \label{MP_inverse}
\end{equation}
Here, $\textbf{B}^{T}$ denotes the transpose of the matrix. This then allows the stokes vector of the incident light to be determined from the measured voltages: $\textbf{B}^{+}\vec{V}=\vec{S}$.

\section{How to Operate}
\begin{figure}[h]
    \centering
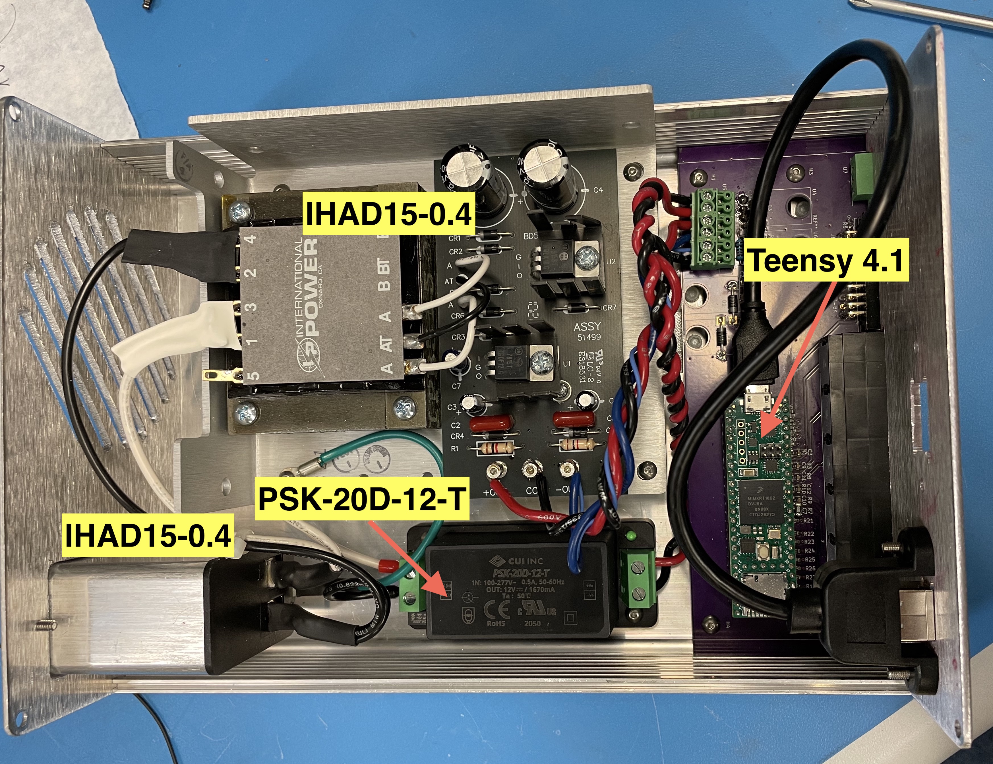
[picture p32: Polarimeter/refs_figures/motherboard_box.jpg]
    
    \caption{The inside of the motherboard box is shown with the power entry module, the two power supplies, and the Teensy labeled with part numbers.}
    \label{motherboard_box}
\end{figure}
The device consists of 3 main components: the optical setup, the motherboard box, and the users computer. The motherboard box, shown in figure \ref{motherboard_box}, contains a Teensy 4.1 microcontroller and two power supplies. The box powers the photodiode detectors and receives 6 voltage signals before communicating them to the user's computer through USB serial. This section will walk through the steps to prepare the device for a measurement. 

\subsection{Optics}
The fiber launch on the polarimeter's optical breadboard is connected to a VOA50-APC variable optical attenuator. This attenuator works for 40nm bands around 1310nm and 1550nm. By turning the screw on the VOA, the input intensity of the light can be adjusted to prevent saturation of the detectors. Each photodiode detecotor will saturate at 130$\mu$W. Therefore, the total input power should be less than $\sim 390\mu$W. 

\subsection{Electronics}
There are two PCB designs used in this device: the Teensy motherboard and the photodiode TIA boards . They were designed in KiCad and the schematics and layouts can be accessed by opening the \verb|.kicab_pro| files.

The 6 photodiode detectors connect to the motherboard box with CAT-5 cables. They need to be connected in order. The connectors on the box are labeled 1 through 6. The detectors should be plugged into the detectors corresponding to the labels in figure \ref{detector_numbers}. 

\begin{figure}[h]
    \centering
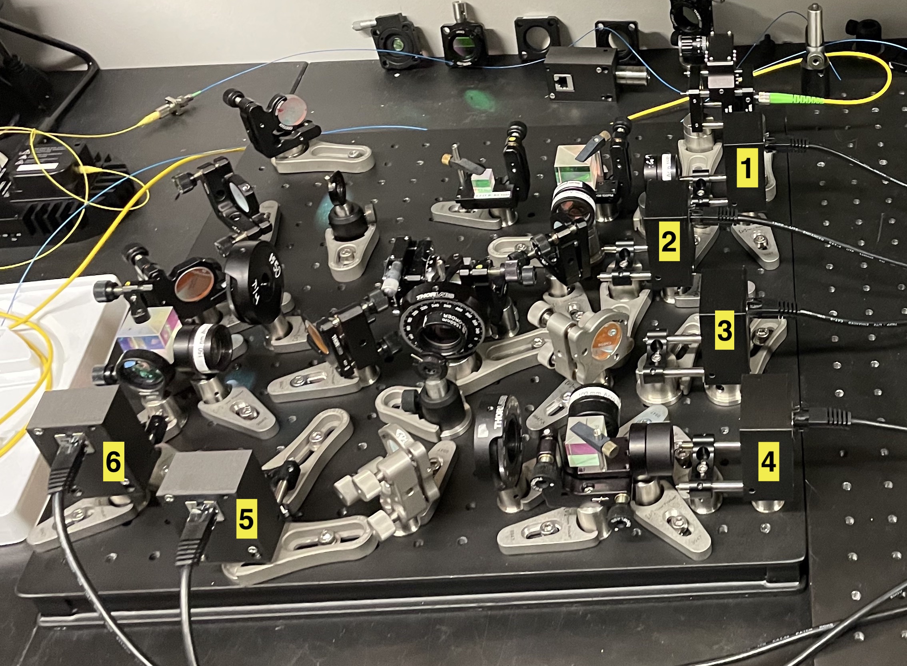
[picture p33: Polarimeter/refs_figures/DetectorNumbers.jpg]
    
    \caption{The detectors should be connected to the motherboard box with this numbering.}
    \label{detector_numbers}
\end{figure}

The box needs to plugged into a wall outlet with a power cord and then connected to a computer by a USB cable.

\subsection{Software}
To operate the device, the Teensy 4.1 in the motherboard box and the user's computer need to be running compatible scripts that communicate through serial. The Teensyduino IDE can be used to upload \verb|.ino| scripts to the microcontroller. This can be downloaded from the \href{https://www.pjrc.com/teensy/td_download.html}{PJRC website}. \verb|SerialParallel.py| and \verb|DriftMeasurement.ino| can be used to make polarization measurements for a specified range of time. \verb|SerialParallel.py| takes the file name for the data and a number of measurements for the detector to take. With the current implementation, the number should be a multiple of 50,000. The device's sample rate is $\sim10$kHz so the number of measurements can be used to roughly set the duration of the measurement. The output of the measurement will be a CSV file containing the 6 voltage measurements from sample. This can be converted to polarization measurements with the most up to date calibration matrix. At the writing of this manual, this matrix is the following. 
 \begin{verbatim}
        Binv = np.matrix([
        [ 0.194, 0.241, 0.255, 0.235, 0.283, 0.273],
        [-0.788, 0.871, 0.0227, 0.0310, -0.0961 ,-0.0594],
        [ 0.110 , -0.142, 0.793, -0.819, 0.103, -0.107],
        [ 1.54, -1.694, 0.524, -0.619, -1.56, 1.97]])
 \end{verbatim}
The text above can be directly copied into a python script to produce a numpy matrix of $\textbf{B}^{+}$. This calibration matrix was calculated on 8/5/2022.

\section{Calibration}
The calibration is done in 2 stages. First, a linear polarizer is used to generate a series of known linear polarization states. The input polarization state can be calculated with the angle of the transmission axis of the polarizer from vertical $\theta$ with Equation \ref{input states}.
\begin{equation}
\vec{S}_{linear} =
\begin{bmatrix}
S_0\\
S_1\\
S_2\\
S_3
\end{bmatrix}=
I(\theta)\begin{bmatrix} 
1\\
-cos(2\theta)\\
sin(2\theta)\\
0
\end{bmatrix}
\label{input states}
\end{equation}
The intensity output from the polarizer will in practice be a function of the rotation angle. From equations \ref{Calibration eq} and \ref{input states}, the $i^{th}$ component of $\Vec{V}$ can be expressed as a linear combination of matrix elements $b_{ij}$. 

\begin{equation}
    v_i = I(\theta) \left( b_{i1} - b_{i2}cos(2\theta) + b_{i3}sin(2\theta) \right)
\end{equation}

The original calibration was done with a linear polarizer with a measured extinction ratio of $>1000:1$ and the orientation of the transmission axis known to $\sim\pm0.25\degree$. The linear polarizer was mounted in a motorized rotation mount and rotated continuously through $360\degree$ at a rate of $1\degree$ per second. The polarimeter recorded measurements at 10,000 Hz. The laser used for this generated linearly polarized light so a waveplate was used to produce circular polarization to input to the polarizer to make intensity of as uniform as possible throughout the measurement. The dependence of the intensity on the polarizer angle could not be completely eliminated so a second data set was taken that measured the intensity after the polarizer as it rotated through $360\degree$s, $I(\theta)$. Then  A chi squared fit to the measured $v_{i}$ was used to determine the $b_{ij}$ matrix elements.

 The second stage of the calibration requires input states with some known ellipticity. For this, a procedure presented in \cite{Azzam89} was used to account for the error in these input states. First, a linear polarizer and a quarter waveplate were aligned with the transmission axis of the former rotated by $45\degree$ from fast axis of the latter. In practice, this produces a nearly circular state. Represented on the Poincare sphere, this state is slightly displaced from one of the poles in figure \ref{Poincare Sphere}. Then, by rotating both the linear polarizer and the quarter waveplate by $90\degree$, the input state is rotated by 180 degrees around the north-south axis of the Poincare sphere. If the initial state was close to circular, then the average of these two states is nearly aligned to the pole of the Poincare sphere and hence a perfect circular state. The input polarization states are linearly related to the voltage states so the voltage states can be averaged to calculate the detectors response to a perfect circular state. To carry out this procedure, $\Vec{V}_1$ and $I_1$, the voltage state and output intensity from the first input state, were measured. After rotating by $90\degree$, $\Vec{V}_2$ and $I_2$ were measured. Then equation \ref{V_circ} was used to calculate the detectors response to normalized circular input state. 
 \begin{equation}
     \Vec{V}_{circ} = \frac{1}{2} \left( \dfrac{\Vec{V_1}}{I_1} + \dfrac{\Vec{V_2}}{I_2} \right)
     \label{V_circ}
 \end{equation}
Then, the last column of the matrix can be calculated.
\begin{equation}
    B_4 = \pm V_{circ} - B_1
    \label{last_col}
\end{equation}
Here, $B_i$ represents that $i^{th}$ column of the instrument matrix and the sign is positive if the circular state generated was right-handed. With the instrument matrix determined, the calibration matrix can be calculate with equation \ref{MP_inverse}. 

For the calibration performed on 5/8/2022, the results are compared to the theoretical values in Figure \ref{calibration Data}. Good agreement can be seen between the theoretical curves and the measured curves for the normalized Stokes parameters. 
\begin{figure}[!h]
\begin{center}
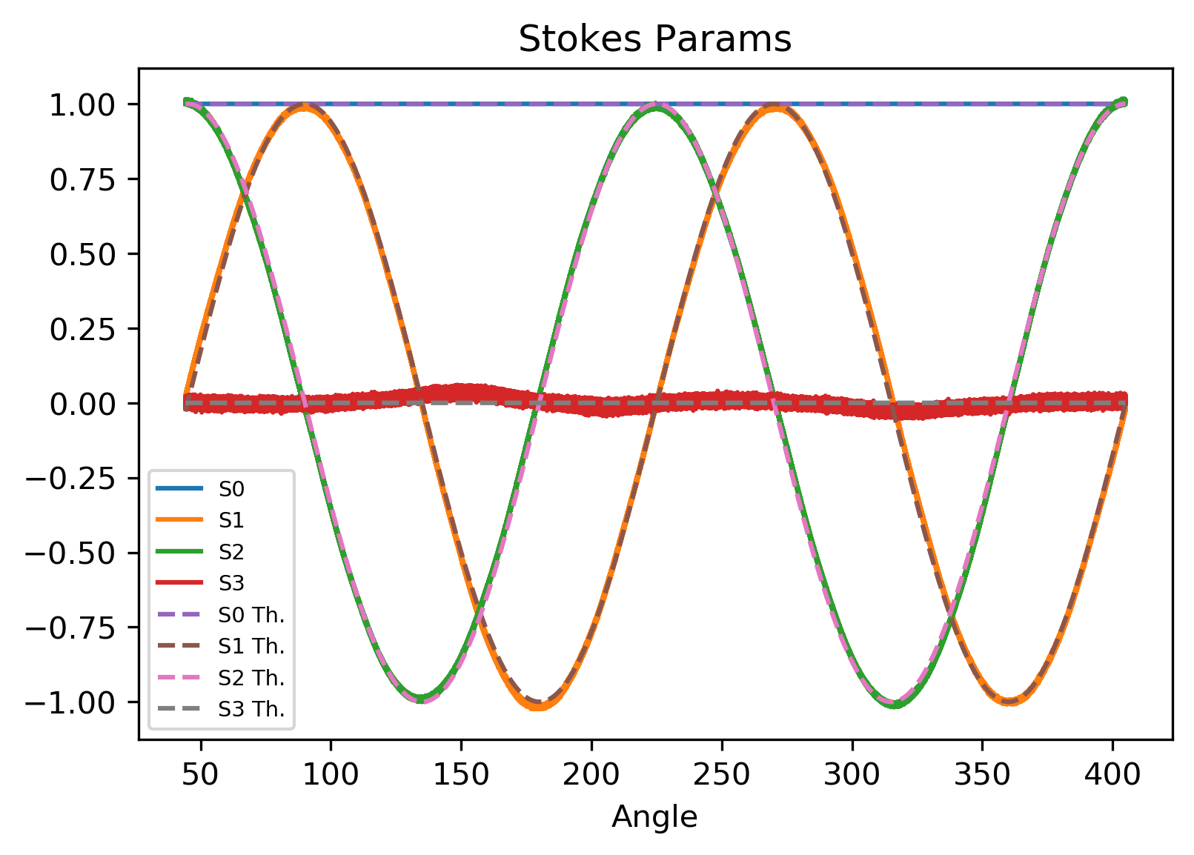
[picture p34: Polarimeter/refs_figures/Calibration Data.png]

\end{center}
\caption{The normalized Stokes parameters are graphed. The measured parameters are solid lines and the theoretical parameters are dotted lines.}
\label{calibration Data}
\end{figure}

\verb|1550 Calibration Analysis Pt 2.ipynb| was used to analyze the data taken during the calibration procedure and calculate the $\textbf{B}^{+}$. \verb|780CalibrationAnalysis.ipynb| was used for 780 nm version of the polarimeter so the calculations can also be referenced. 

\section{Notes}
\subsection{Calibration and wavelength dependence}
The waveplates in used are a mix of single and multi order waveplates. Therefore, the device is expected to have wavelength dependent performance and should be calibrated on the wavelength needed for a measurement. This may be improved by replacing the waveplates with achromatic waveplates. 
\subsection{Teensyduino IDE}
The Teensyduino IDE is a valuable tool for working with the polarimeter. It allows for simple serial communication between the user's computer and the Teensy. The Serial Monitor and Serial Plotter functions allowed for the data sent from the Teensy to be visualized and plotted. \verb|Photodiode_Mode.ino| sends the voltages from each photodiode to the user's computer in the so that the Serial Plotter will automatically plot these values as a funtion of time. This has many use cases, including tuning the input power so that none of the photodiodes saturate.

\section{Acknowledgements}
This device was built during the summer of 2022 in the Rubidium Rydberg lab with advisors Dr. Steven Rolston and Dr. Trey Porto. Credit and thanks are owed to Patrick Banner for his involvement and mentroship and Dr. Alessandro Restelli for his invaluable electronics help.

\printbibliography
\end{document}

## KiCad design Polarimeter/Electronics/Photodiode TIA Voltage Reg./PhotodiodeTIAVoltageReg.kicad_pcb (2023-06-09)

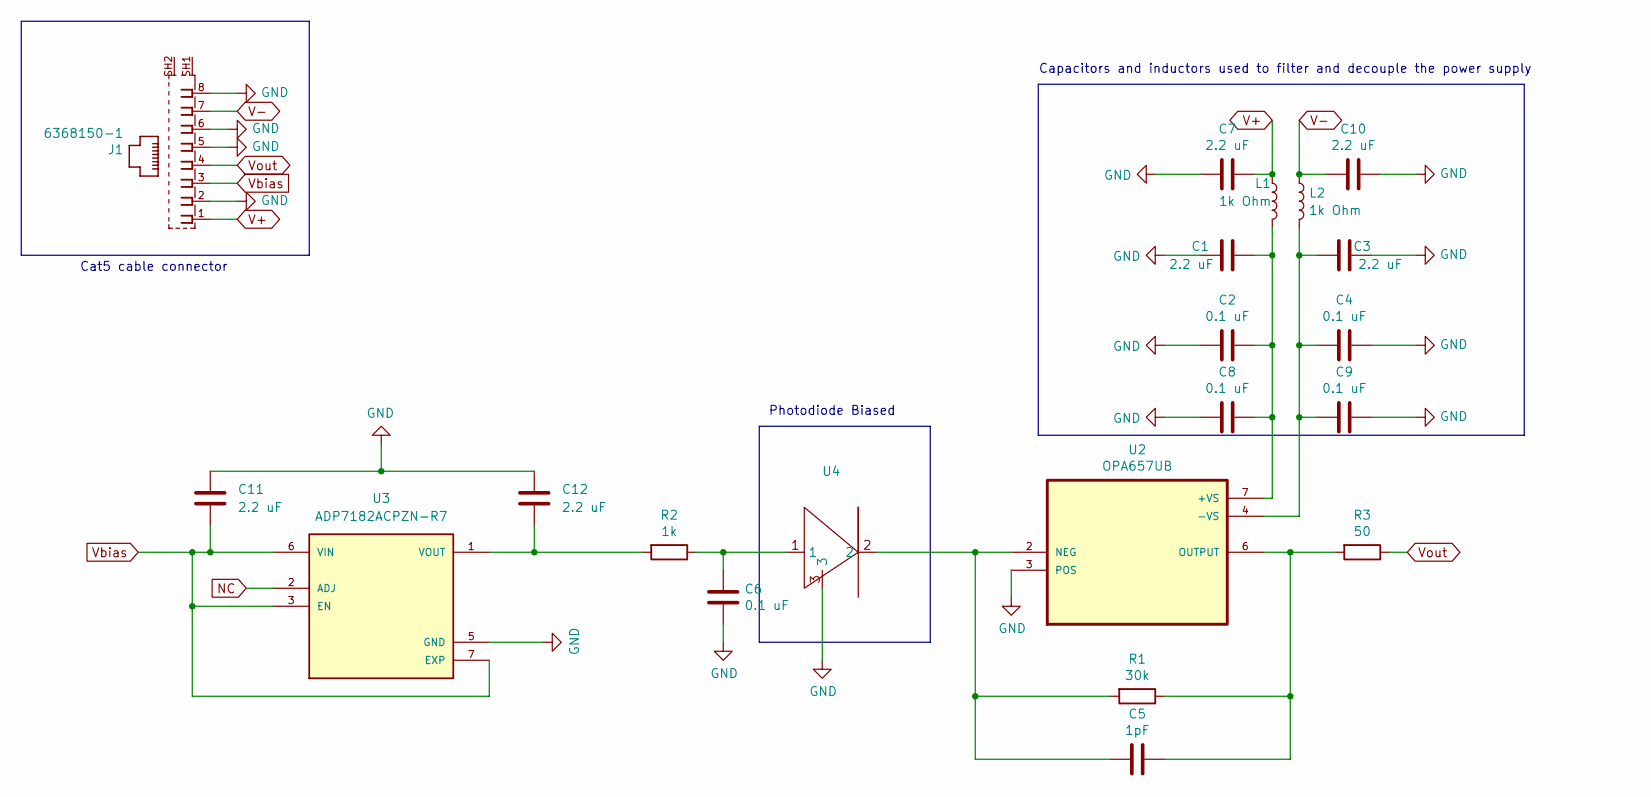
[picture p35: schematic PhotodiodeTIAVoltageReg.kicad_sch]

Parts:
C1, C3, C7, C10, C11, C12: 2.2 uF; C_0805_2012Metric
C2, C4, C6, C8, C9: 0.1 uF; C_0603_1608Metric
C5: 1pF; C_0603_1608Metric
J1: 6368150-1; TE_6368150-1
L1, L2: 1k Ohm; L_0603_1608Metric
R1: 30k; R_0603_1608Metric
R2: 1k; R_0603_1608Metric
R3: 50; R_0603_1608Metric
U2: OPA657UB; SOIC127P599X175-8N
U3: ADP7182ACPZN-R7; SON65P200X200X65-7N
U4: (no value)

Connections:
GND: C1.2, C2.2, C3.1, C4.2, C6.2, C7.2, C8.2, C9.2, C10.1, C11.1, C12.1, J1.2, J1.5, J1.6, J1.8, U2.3 (POS), U3.5 (GND), U4.3
NC: U3.2 (ADJ)
unnamed: C1.1, C2.1, C8.1, L1.2, U2.7 (+VS)
unnamed: C3.2, C4.1, C9.1, L2.2, U2.4 (-VS)
unnamed: C5.1, R1.2, U2.2 (NEG), U4.2
unnamed: C5.2, R1.1, R3.2, U2.6 (OUTPUT)
unnamed: C6.1, R2.1, U4.1
unnamed: C12.2, R2.2, U3.1 (VOUT)
V+: C7.1, J1.1, L1.1
V-: C10.2, J1.7, L2.1
Vbias: C11.2, J1.3, U3.3 (EN), U3.6 (VIN), U3.7 (EXP)
Vout: J1.4, R3.1

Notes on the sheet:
Cat5 cable connector
Capacitors and inductors used to filter and decouple the power supply
Photodiode Biased

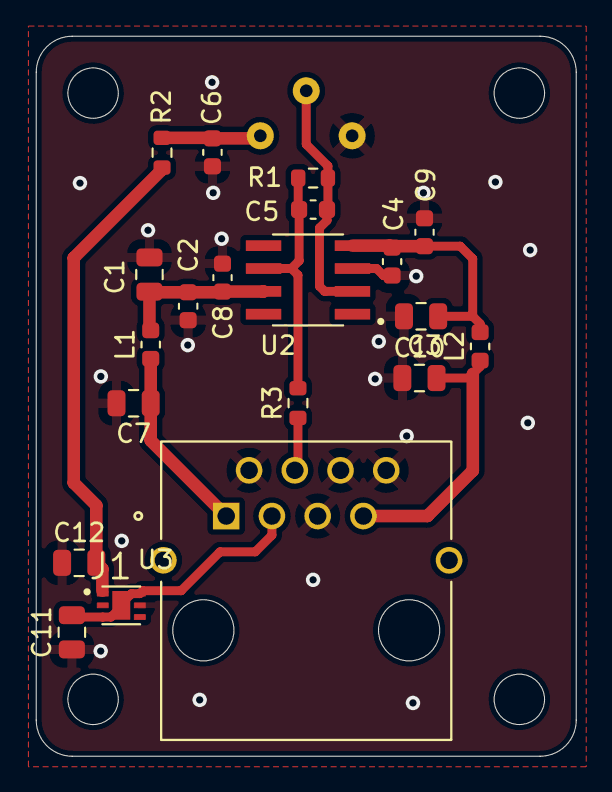
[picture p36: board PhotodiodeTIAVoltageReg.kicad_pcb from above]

Board: 2 copper layers, 30.0 x 40.0 mm, 21 parts (1 on the bottom side), 11 nets.

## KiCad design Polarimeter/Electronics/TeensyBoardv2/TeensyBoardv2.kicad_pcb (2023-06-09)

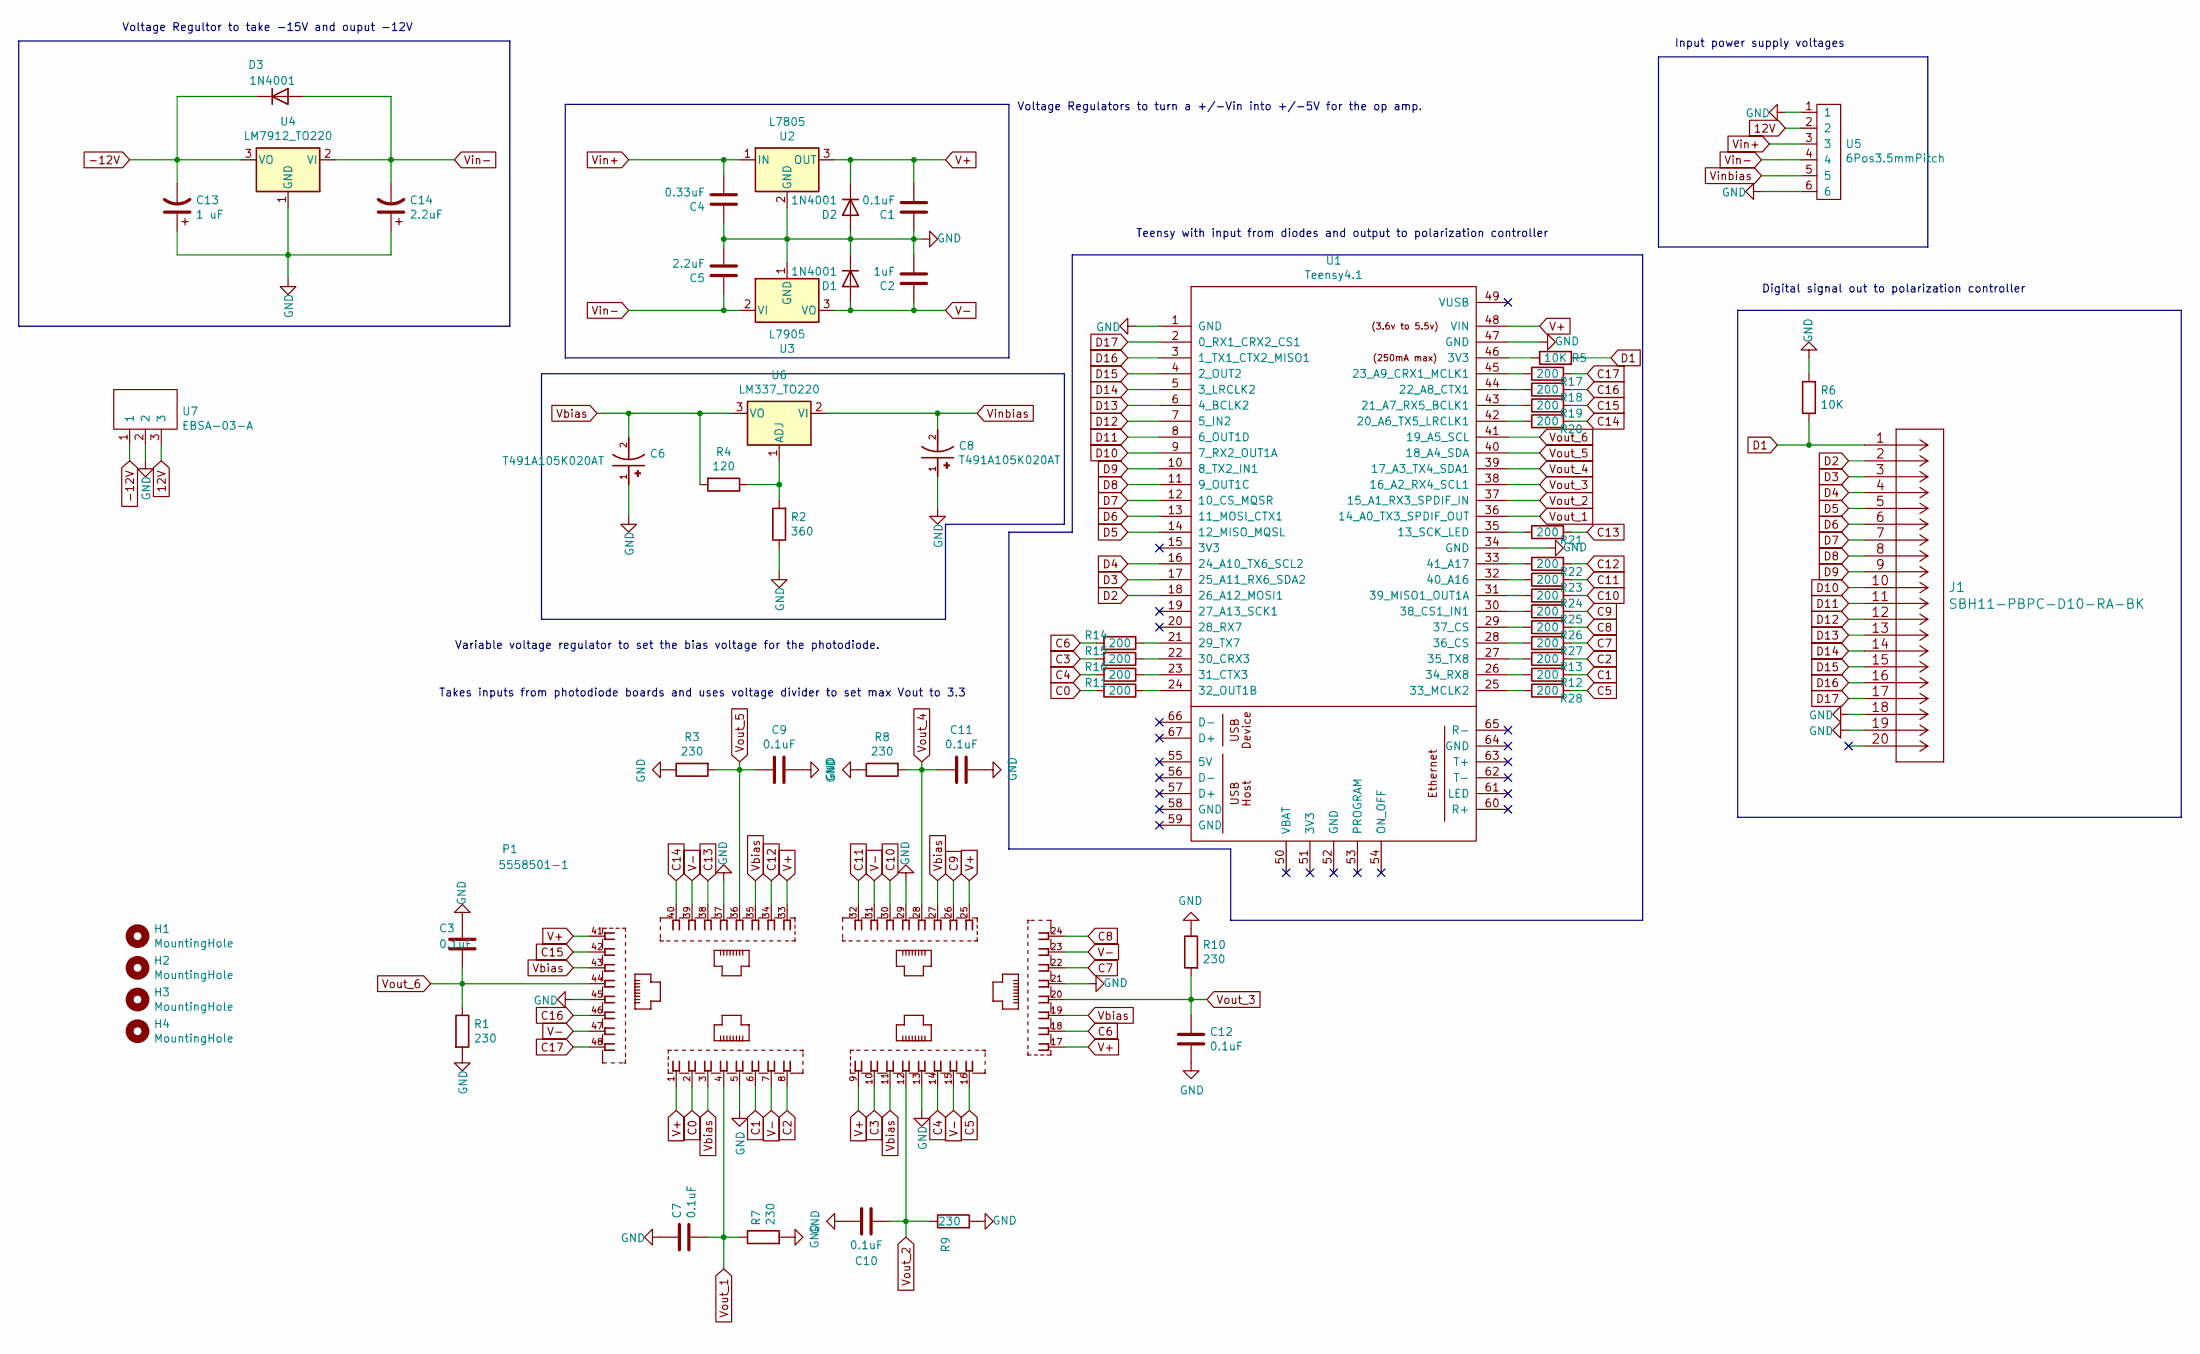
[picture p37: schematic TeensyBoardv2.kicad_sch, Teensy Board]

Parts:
C1, C3, C7, C9, C10, C11, C12: 0.1uF; C_0603_1608Metric
C2: 1uF; C_0603_1608Metric
C4: 0.33uF; C_0603_1608Metric
C5: 2.2uF; C_0603_1608Metric
C6, C8: T491A105K020AT; CAPMP3216X180N; PARTREV N/A
C13: 1 uF; CPol_0603_1608Metric
C14: 2.2uF; CPol_0603_1608Metric
D1, D2, D3: 1N4001; D_DO-41_SOD81_P10.16mm_Horizontal
H1, H2, H3, H4: MountingHole; MountingHole_3.5mm
J1: SBH11-PBPC-D10-RA-BK
P1: 5558501-1
R1, R3, R7, R8, R9, R10: 230; R_0603_1608Metric
R2: 360; R_0603_1608Metric
R4: 120; R_0603_1608Metric
R5, R6: 10K; R_0603_1608Metric
R11, R12, R13, R14, R15, R16, R17, R18, R19, R20, R21, R22, R23, R24, R25, R26, R27, R28: 200; R_0603_1608Metric
U1: Teensy4.1; Teensy41
U2: L7805; TO-220F-3_UnderBoardMount
U3: L7905; TO-220F-3_UnderBoardMount
U4: LM7912_TO220; TO-220F-3_UnderBoardMount
U5: 6Pos3.5mmPitch; 6Pos 3.5mmPitch
U6: LM337_TO220; TO-220F-3_UnderBoardMount
U7: EBSA-03-A

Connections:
12V: U5.2, U7.3
-12V: C13.2, D3.1 (K), U4.3 (VO), U7.1
C0: P1.2, R11.2
C1: P1.6, R12.2
C2: P1.8, R13.2
C3: P1.10, R15.2
C4: P1.14, R16.2
C5: P1.16, R28.2
C6: P1.18, R14.2
C7: P1.22, R27.2
C8: P1.24, R26.2
C9: P1.26, R25.2
C10: P1.30, R24.2
C11: P1.32, R23.2
C12: P1.34, R22.2
C13: P1.38, R21.2
C14: P1.40, R20.2
C15: P1.42, R19.2
C16: P1.46, R18.2
C17: P1.48, R17.2
D1: J1.1, R5.2, R6.1
D2: J1.2, U1.18 (26_A12_MOSI1)
D3: J1.3, U1.17 (25_A11_RX6_SDA2)
D4: J1.4, U1.16 (24_A10_TX6_SCL2)
D5: J1.5, U1.14 (12_MISO_MQSL)
D6: J1.6, U1.13 (11_MOSI_CTX1)
D7: J1.7, U1.12 (10_CS_MQSR)
D8: J1.8, U1.11 (9_OUT1C)
D9: J1.9, U1.10 (8_TX2_IN1)
D10: J1.10, U1.9 (7_RX2_OUT1A)
D11: J1.11, U1.8 (6_OUT1D)
D12: J1.12, U1.7 (5_IN2)
D13: J1.13, U1.6 (4_BCLK2)
D14: J1.14, U1.5 (3_LRCLK2)
D15: J1.15, U1.4 (2_OUT2)
D16: J1.16, U1.3 (1_TX1_CTX2_MISO1)
D17: J1.17, U1.2 (0_RX1_CRX2_CS1)
GND: C1.1, C2.2, C3.1, C4.1, C5.2, C6.1, C7.1, C8.1, C9.2, C10.1, C11.2, C12.2, C13.1, C14.1, D1.1 (K), D2.2 (A), J1.18, J1.19, P1.5, P1.13, P1.21, P1.29, P1.37, P1.45, R1.2, R2.1, R3.1, R6.2, R7.2, R8.1, R9.2, R10.1, U1.1 (GND), U1.34 (GND), U1.47 (GND), U2.2 (GND), U3.1 (GND), U4.1 (GND), U5.1, U5.6, U7.2
unnamed: R2.2, R4.1, U6.1 (ADJ)
unnamed: R5.1, U1.46 (3V3)
unnamed: R11.1, U1.24 (32_OUT1B)
unnamed: R12.1, U1.26 (34_RX8)
unnamed: R13.1, U1.27 (35_TX8)
unnamed: R14.1, U1.21 (29_TX7)
unnamed: R15.1, U1.22 (30_CRX3)
unnamed: R16.1, U1.23 (31_CTX3)
unnamed: R17.1, U1.45 (23_A9_CRX1_MCLK1)
unnamed: R18.1, U1.44 (22_A8_CTX1)
unnamed: R19.1, U1.43 (21_A7_RX5_BCLK1)
unnamed: R20.1, U1.42 (20_A6_TX5_LRCLK1)
unnamed: R21.1, U1.35 (13_SCK_LED)
unnamed: R22.1, U1.33 (41_A17)
unnamed: R23.1, U1.32 (40_A16)
unnamed: R24.1, U1.31 (39_MISO1_OUT1A)
unnamed: R25.1, U1.30 (38_CS1_IN1)
unnamed: R26.1, U1.29 (37_CS)
unnamed: R27.1, U1.28 (36_CS)
unnamed: R28.1, U1.25 (33_MCLK2)
V+: C1.2, D2.1 (K), P1.1, P1.9, P1.17, P1.25, P1.33, P1.41, U1.48 (VIN), U2.3 (OUT)
V-: C2.1, D1.2 (A), P1.7, P1.15, P1.23, P1.31, P1.39, P1.47, U3.3 (VO)
Vbias: C6.2, P1.3, P1.11, P1.19, P1.27, P1.35, P1.43, R4.2, U6.3 (VO)
Vin+: C4.2, U2.1 (IN), U5.3
Vin-: C5.1, C14.2, D3.2 (A), U3.2 (VI), U4.2 (VI), U5.4
Vinbias: C8.2, U5.5, U6.2 (VI)
Vout_1: C7.2, P1.4, R7.1, U1.36 (14_A0_TX3_SPDIF_OUT)
Vout_2: C10.2, P1.12, R9.1, U1.37 (15_A1_RX3_SPDIF_IN)
Vout_3: C12.1, P1.20, R10.2, U1.38 (16_A2_RX4_SCL1)
Vout_4: C11.1, P1.28, R8.2, U1.39 (17_A3_TX4_SDA1)
Vout_5: C9.1, P1.36, R3.2, U1.40 (18_A4_SDA)
Vout_6: C3.2, P1.44, R1.1, U1.41 (19_A5_SCL)

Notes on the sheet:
Voltage Regulators to turn a +/-Vin into +/-5V for the op amp.
Input power supply voltages
Variable voltage regulator to set the bias voltage for the photodiode.
Digital signal out to polarization controller
Takes inputs from photodiode boards and uses voltage divider to set max Vout to 3.3
Teensy with input from diodes and output to polarization controller
Voltage Regultor to take -15V and ouput -12V

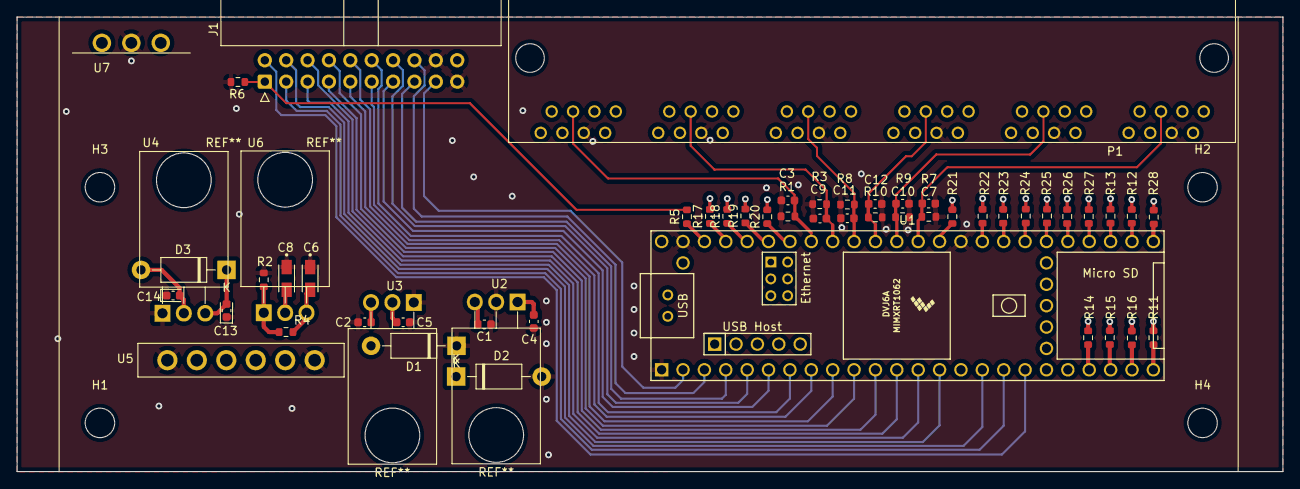
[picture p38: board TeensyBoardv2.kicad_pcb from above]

Board: 4 copper layers, 150.4 x 54.0 mm, 58 parts (0 on the bottom side), 70 nets.

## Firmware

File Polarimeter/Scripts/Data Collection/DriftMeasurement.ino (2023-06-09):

//Define pins for input here
int pin1 = 14;
int pin2 = 15;
int pin3 = 16;
int pin4 = 17;
int pin5 = 18;
int pin6 = 19;

//unsigned long samples = 10000*10;
unsigned long Tstart;
unsigned long Tstop;
void setup() {
  // put your setup code here, to run once:
  Serial.begin(115200);
  pinMode(pin1, INPUT);
  pinMode(pin2, INPUT);
  pinMode(pin3, INPUT);
  pinMode(pin4, INPUT);
  pinMode(pin5, INPUT);
  pinMode(pin6, INPUT);
}

void loop() {
  if(Serial.available()>0){
      unsigned int samples = Serial.readString().toInt();
      unsigned int i = 0;
       union data_union {
       struct data_struct{
        int startChar;
        unsigned int timeStamp;
        int V1;
        int V2;
        int V3;
        int V4;
        int V5;
        int V6;
        int endChar;
        } data;
        char buf[sizeof(data)];
       } record;

       record.data.startChar = -100;
       record.data.endChar = -200;
       Tstart = millis();
       
      while(i < samples){
        record.data.timeStamp = micros();
        record.data.V1 = analogRead(pin1);
        record.data.V2 = analogRead(pin2);
        record.data.V3 = analogRead(pin3);
        record.data.V4 = analogRead(pin4);
        record.data.V5 = analogRead(pin5); 
        record.data.V6 = analogRead(pin6);
        Serial.write(record.buf,sizeof(record.data));
        i++;
      }
    }

}
